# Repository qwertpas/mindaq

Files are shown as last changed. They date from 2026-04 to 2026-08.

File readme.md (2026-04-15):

# mindaq PCB

A cheap and minimal data aquisition system for reading 6-axis force/torque sensors at high rates.

demo

- 2.5V strain gauge excitation using precision reference (REF5025)
- Simultaneous sampling 24-bit ADC (ADS131M08) with 8 channels at 32k samples/second for
    - 6x strain gauges
    - 1x voltage up to 29.4V 
    - 1x current using external low-side shunt resistor
- Controlled by ESP32S3 Supermini dev board (USB-C powered)
- Display live force/torque data on Adafruit color TFT
- 42 x 29 mm board size
- 2-layer, single side components, JLCPCB economic assembly
- About $11 in parts cost per board (including ESP32S3)
- Single order of 2pcs is $70, 5pcs is $120 including everything (shipping and customs about doubles the cost!) 

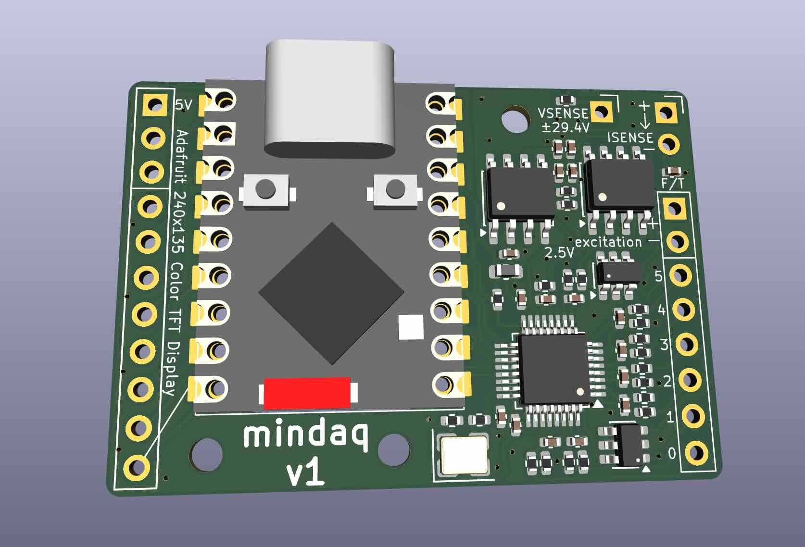
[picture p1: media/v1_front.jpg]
Front Side

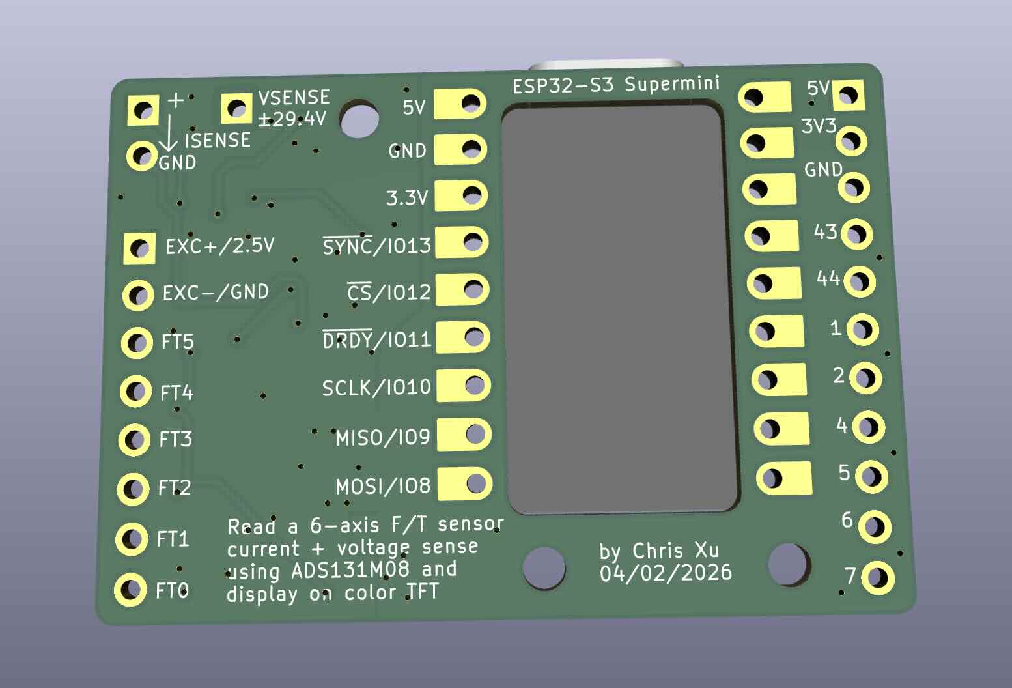
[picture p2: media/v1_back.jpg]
Back Side


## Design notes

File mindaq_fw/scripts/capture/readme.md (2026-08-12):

# Mindaq Capture GUI

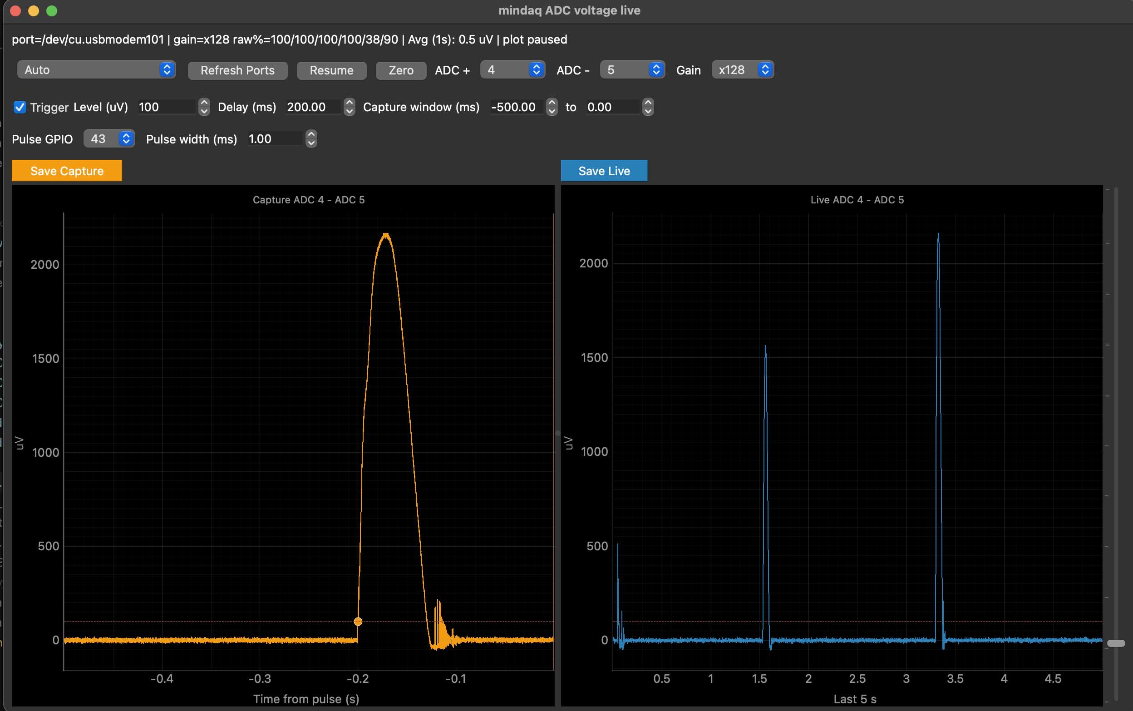
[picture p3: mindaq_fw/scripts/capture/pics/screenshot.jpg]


This GUI streams voltage data from the Mindaq, shows a live rolling plot, and records trigger-aligned captures like an oscilloscope. It also pulses a GPIO pin a configurable delay after the trigger to align external devices (e.g. slow motion camera). Mindaq must be running the capture firmware.

## Usage

Download [capture_gui.py](https://github.com/qwertpas/mindaq/blob/main/mindaq_fw/scripts/capture/capture_gui.py).

Install python libraries if you don't have them:

```bash
python3 -m pip install pyserial pyqtgraph PyQt5
```

Start the GUI:

```bash
python3 capture_gui.py
```

If this does not work on Windows, try replacing `python3` in the above commands with `py -3`.

## Plots

- Live plot (orange): shows the selected ADC voltage over the last 5 seconds. Data is displayed at 1 kHz.
- Capture plot (blue): shows the most recent trigger capture, aligned so GPIO pulse start is at time 0. Data is displayed at 1 kHz.

## Buttons and Settings

- Zeroing: Sets a baseline voltage as a 0 reading by subtracting the average voltage over the last 1 second.
- ADC + and ADC -: select the ADC channels to read from. Channels 6 and 7 are labeled Isense and Vsense. If two channels are selected, the difference is used (useful for load cells).
- Gain: sets the ADC amplifier gain between 1x and 128x. Higher gain means more sensitivity, but could saturate the reading if the voltage is too high (e.g. very high force applied). Check for saturation by looking at the raw% values or whether the live plot is clipping.
- Trigger level: set in microvolts using the numeric field or vertical slider.
- Delay: this amount of time after the trigger threshold crossing, the GPIO pulse starts and is used as the reference for when `capture_time_s` = 0.
- Capture window: you can configure the time window to display and save before and after `capture_time_s` = 0. Default is -500ms to 0ms, meaning it saves and displays the last 500ms before the GPIO pulse start.
- Pulse GPIO: select the GPIO pin to pulse. See labels on the [back of the PCB](https://github.com/qwertpas/mindaq/blob/main/media/v1_back.jpg).
- Pulse width: configurable duration of the GPIO pulse.
- Save Capture: saves the capture window at full 32 kHz sampling rate.
- Save Live: saves the current live buffer at full 32 kHz sampling rate.
- The firmware turns on the built-in red LED when a trigger is accepted and turns it off when the pulse is done.

## Saved CSV data format

Basic:
- `capture_time_s`: time relative to the GPIO pulse start (trigger threshold crossing plus the configured delay). 0 matches the red pulse-start line in the capture plot. The events you care about are likely when `capture_time_s` is slightly negative. <u>Use this to align external devices (e.g. slow motion camera).</u>
- `voltage_zeroed_uv`: Measured voltage after subtracting the current zero offset.
- `voltage_uv`: Measured voltage before zeroing.
- `device_time_s`: Mindaq precise device time since it was powered on.
- `datetime`: wall-clock timestamp estimated from the computer time when saved, used to check roughly when experiment was done. Not as accurate, use `device_time_s` or `capture_time_s` instead for precise timing.

Capture timing columns:
- `trigger_time_s`: device time when the signal crossed the trigger threshold.
- `pulse_start_time_s`: device time when the GPIO pulse starts.
- `pulse_end_time_s`: device time when the GPIO pulse ends.
- `trigger_threshold_uv`: trigger threshold.
- `trigger_cross`: `1` on the sample nearest the trigger crossing.
- `pulse_start`: `1` on the sample nearest pulse start.
- `pulse_active`: `1` for samples during the pulse if the capture window includes them.
- `trigger_gpio`: selected output pin.
- `trigger_edge`: currently always `Rising`, but noise makes it activate on falling edges too.

For debugging:
- `seq`: sample sequence number.
- `pos_channel`, `neg_channel`: selected ADC inputs.
- `adc_N_uv`, `adc_N_raw`: per-channel microvolts and raw ADC counts, paired by channel. ADC 6 is Isense and ADC 7 is Vsense.
- `gain_code`, `warn_flags`, `clip_flags`: stream metadata.

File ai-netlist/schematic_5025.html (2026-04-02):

# minDAQ · Visual Schematic · netlist_5025

ADS131M08 8-ch ADC · 6-ch Force/Torque · ESP32-S3 SuperMini · REF5025 · OPA2333 · SiTime 8.192 MHz

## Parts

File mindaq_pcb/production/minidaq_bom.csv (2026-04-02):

Designator | Footprint | Quantity | Value | LCSC Part #
C1, C11, C2, C3, C4, C7 | 0402 | 6 | 1uF | C52923
C12, C13, C14, C15, C16, C18, C8 | 0402 | 7 | 10nF | C15195
C17 | 0402 | 1 | 1nF | C1523
C5 | 0402 | 1 | 10uF | C15525
C6 | 0402 | 1 | 220nF | C16772
C9 | 0402 | 1 | 0.1uF | C307331
FB1 | 0603 | 1 | BLM18PG121SN1D | C14709
R1 | 0402 | 1 | 33R | C25105
R10, R11, R12, R13, R14, R15, R16, R17, R20, R21, R5, R6, R8, R9 | 0402 | 14 | 100R | C25076
R18, R2, R3, R4, R7 | 0402 | 5 | 47k | C25792
R19 | 0402 | 1 | 2k | C4109
U1 | TQFP-32_5x5mm_P0.5mm | 1 | ADS131M08IPBSR | C2862610
U3 | SOIC-8_3.9x4.9mm_P1.27mm | 1 | REF5025AIDR | C11341
U4 | SOIC-8_3.9x4.9mm_P1.27mm | 1 | OPA2333AIDR | C38732
Y1 | Crystal_SMD_3225-4Pin_3.2x2.5mm | 1 | MST8011AI-22-33E8.192000 | C51026284

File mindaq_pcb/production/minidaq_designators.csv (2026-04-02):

C1:1
C11:1
C12:1
C13:1
C14:1
C15:1
C16:1
C17:1
C18:1
C2:1
C3:1
C4:1
C5:1
C6:1
C7:1
C8:1
C9:1
FB1:1
H1:1
H2:1
H3:1
J1:1
J2:1
J3:1
J6:1
NT1:1
NT2:1
R1:1
R10:1
R11:1
R12:1
R13:1
R14:1
R15:1
R16:1
R17:1
R18:1
R19:1
R2:1
R20:1
R21:1
R3:1
R4:1
R5:1
R6:1
R7:1
R8:1
R9:1
U1:1
U2:1
U3:1
U4:1
U5:1
U6:1
Y1:1

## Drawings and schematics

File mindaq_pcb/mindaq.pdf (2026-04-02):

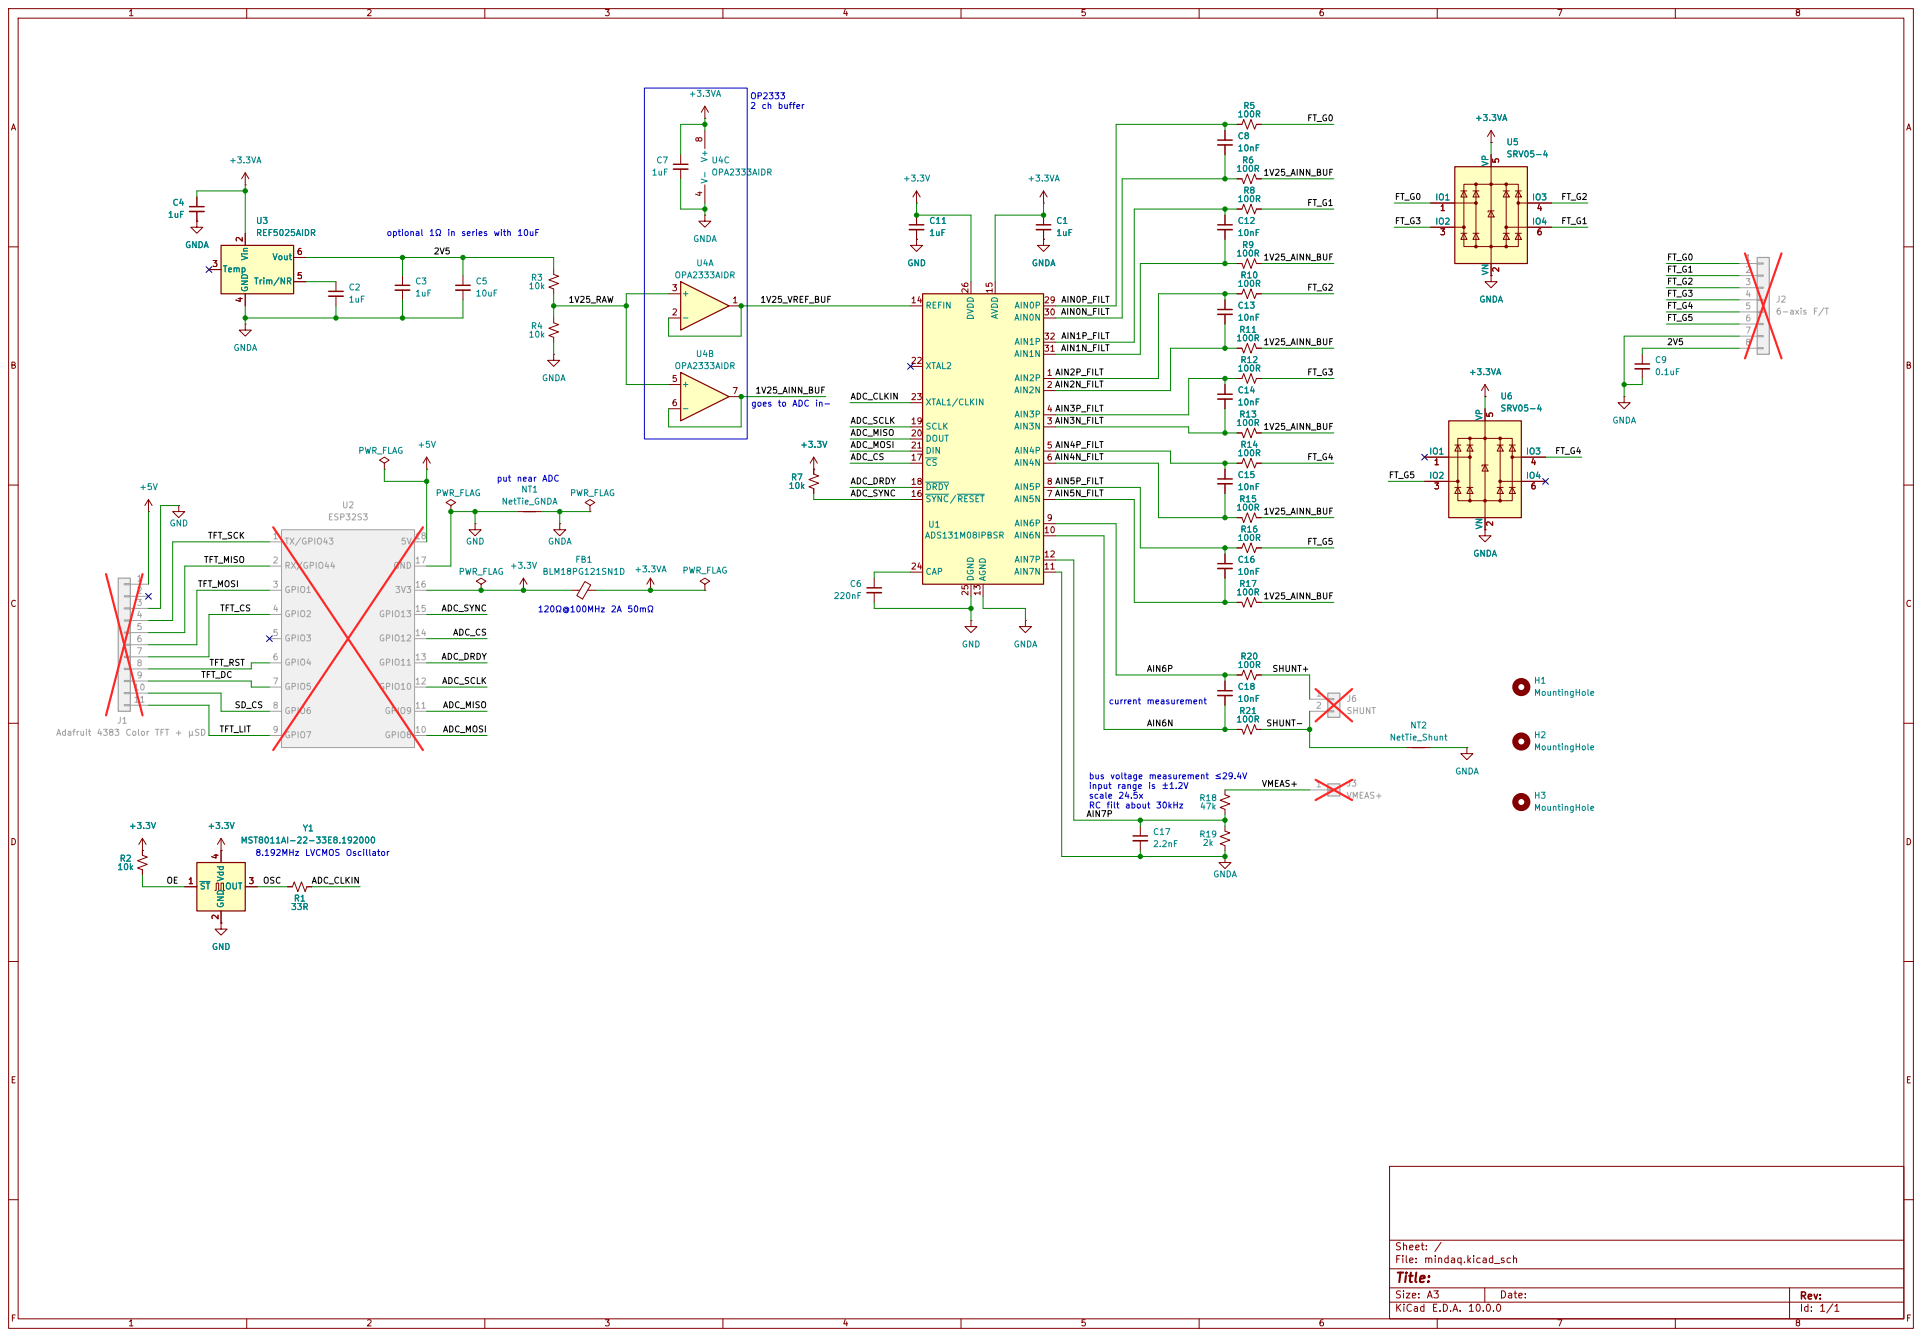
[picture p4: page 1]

2 ch buffer optional 1Ω in series with 10uF

goes to ADC in-

current measurement bus voltage measurement ≤29.4V

Adafruit 4383 Color TFT + μSD

input range is ±1.2V
scale 24.5x RC filt about 30kHz

Size: A3 | Rev: | F Date:
KiCad E.D.A. 10.0.0 | Id: 1/1

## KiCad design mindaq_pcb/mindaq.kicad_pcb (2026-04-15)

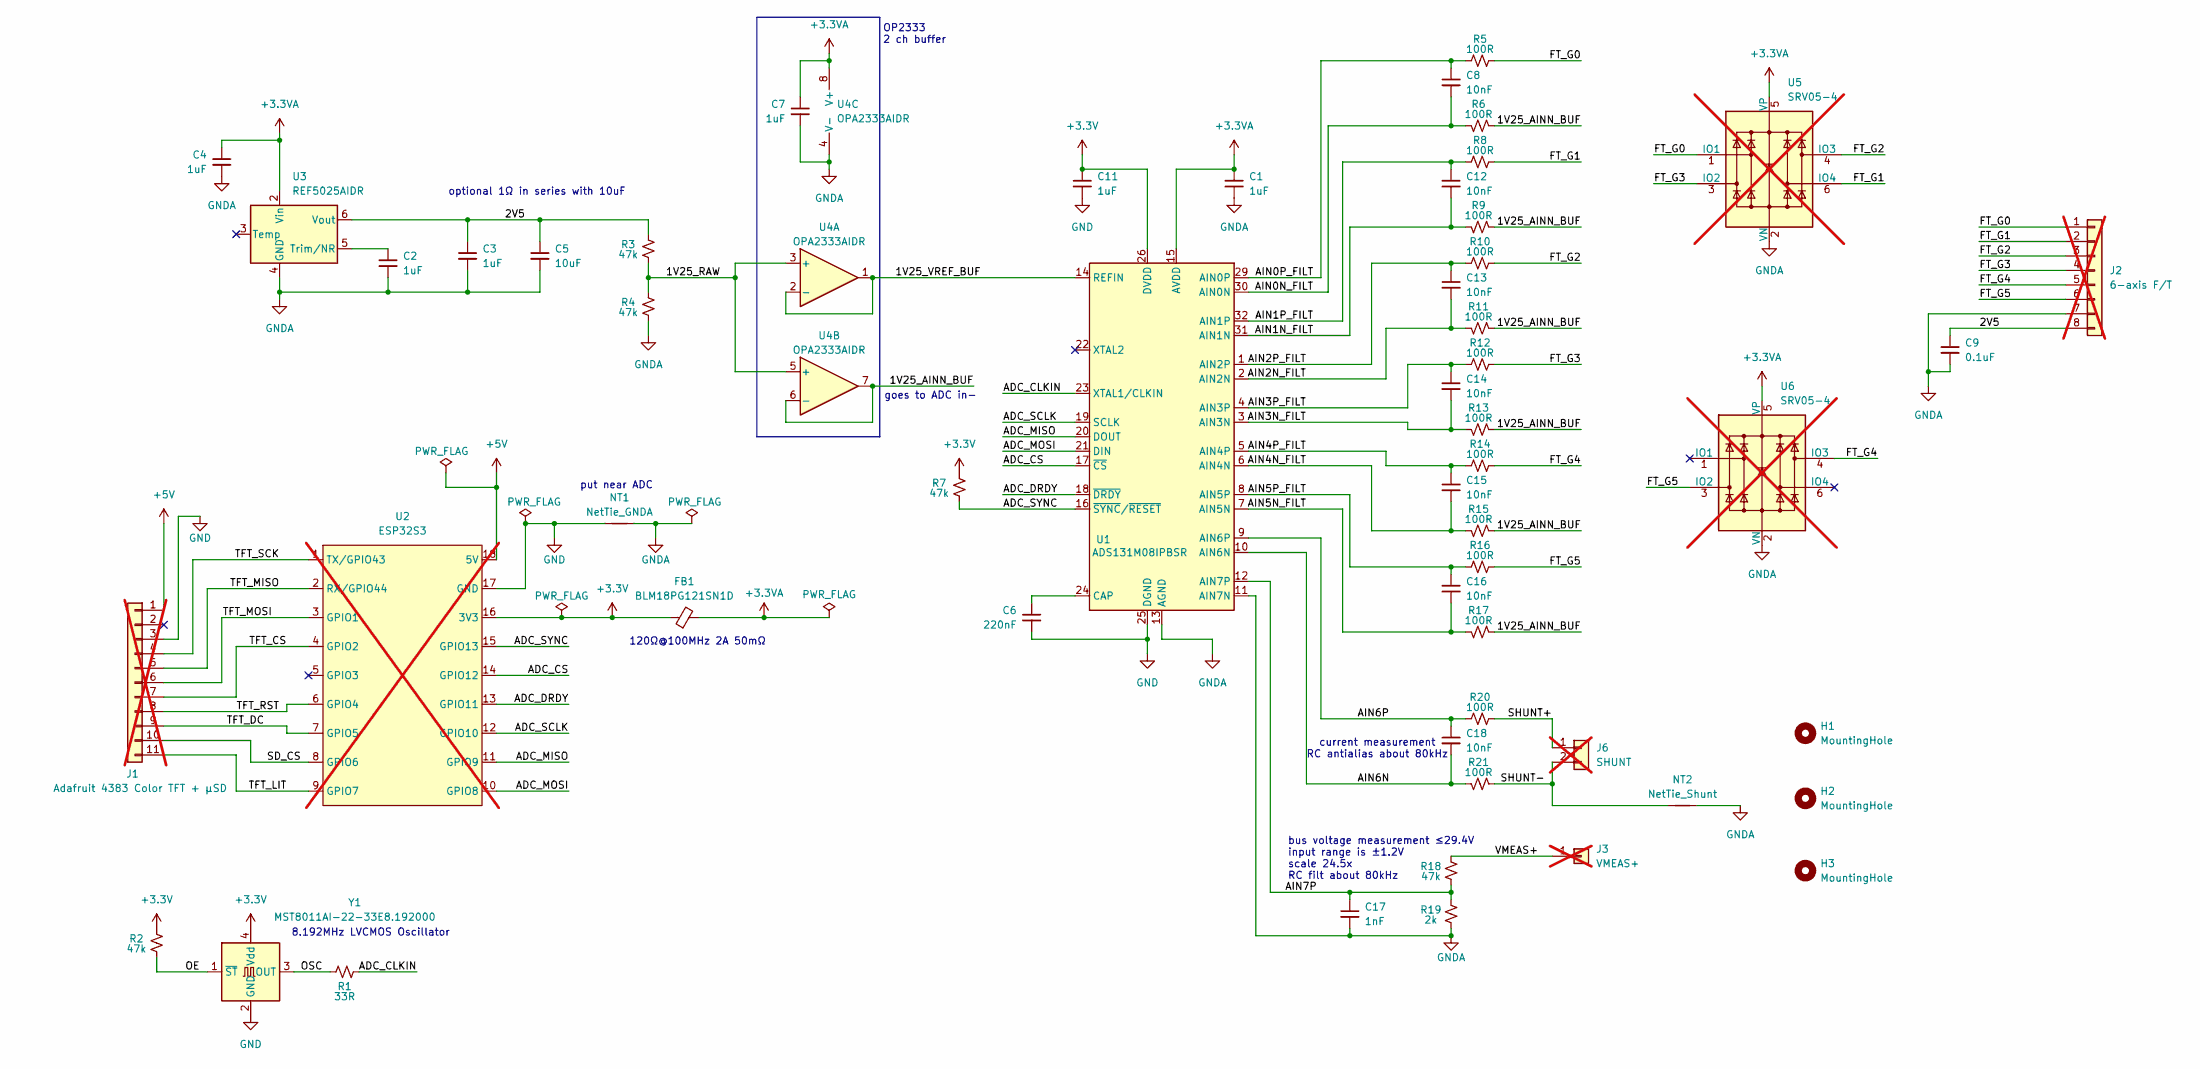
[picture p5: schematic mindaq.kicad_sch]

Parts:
C1, C2, C3, C4, C7, C11: 1uF; C_0402_1005Metric; LCSC C52923
C5: 10uF; C_0402_1005Metric; LCSC C15525
C6: 220nF; C_0402_1005Metric; LCSC C16772
C8, C12, C13, C14, C15, C16, C18: 10nF; C_0402_1005Metric; LCSC C15195
C9: 0.1uF; C_0402_1005Metric; LCSC C307331
C17: 1nF; C_0402_1005Metric; LCSC C1523
FB1: BLM18PG121SN1D; L_0603_1608Metric; LCSC C14709
H1, H2, H3: MountingHole; MountingHole_2.2mm_M2
J1: Adafruit 4383 Color TFT + μSD; PinSocket_1x11_P2.54mm_Vertical; not fitted
J2: 6-axis F/T; PinSocket_1x08_P2.54mm_Vertical; not fitted
J3: VMEAS+; PinSocket_1x01_P2.54mm_Vertical; not fitted
J6: SHUNT; PinSocket_1x02_P2.54mm_Vertical; not fitted
NT1: NetTie_GNDA; NetTie-2_SMD_Pad2.0mm
NT2: NetTie_Shunt; NetTie-2_SMD_Pad0.5mm
R1: 33R; R_0402_1005Metric; LCSC C25105
R2, R3, R4, R7, R18: 47k; R_0402_1005Metric; LCSC C25792
R5, R6, R8, R9, R10, R11, R12, R13, R14, R15, R16, R17, R20, R21: 100R; R_0402_1005Metric; LCSC C25076
R19: 2k; R_0402_1005Metric; LCSC C4109
U1: ADS131M08IPBSR; TQFP-32_5x5mm_P0.5mm; LCSC C2862610
U2: ESP32S3; esp32s3-supermini; not fitted
U3: REF5025AIDR; SOIC-8_3.9x4.9mm_P1.27mm; LCSC C11341
U4: OPA2333AIDR; SOIC-8_3.9x4.9mm_P1.27mm; LCSC C38732
U5, U6: SRV05-4; SOT-23-6; LCSC C20615829; not fitted
Y1: MST8011AI-22-33E8.192000; Crystal_SMD_3225-4Pin_3.2x2.5mm; LCSC C51026284

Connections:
+3.3V: C11.1, FB1.1, R2.1, R7.1, U1.26 (DVDD), U2.16 (3V3), Y1.4 (Vdd)
+3.3VA: C1.1, C4.1, C7.1, FB1.2, U1.15 (AVDD), U3.2 (Vin), U4.8 (V+), U5.5 (VP), U6.5 (VP)
+5V: J1.1, U2.18 (5V)
/1V25_AINN_BUF: R6.2, R9.2, R11.2, R13.2, R15.2, R17.2, U4.6 (-), U4.7
/1V25_RAW: R3.2, R4.1, U4.3 (+), U4.5 (+)
/1V25_VREF_BUF: U1.14 (REFIN), U4.1, U4.2 (-)
/2V5: C3.1, C5.1, C9.1, J2.8, R3.1, U3.6 (Vout)
/ADC_CLKIN: R1.1, U1.23 (XTAL1/CLKIN)
/ADC_CS: U1.17 (~CS), U2.14 (GPIO12)
/ADC_DRDY: U1.18 (~DRDY), U2.13 (GPIO11)
/ADC_MISO: U1.20 (DOUT), U2.11 (GPIO9)
/ADC_MOSI: U1.21 (DIN), U2.10 (GPIO8)
/ADC_SCLK: U1.19 (SCLK), U2.12 (GPIO10)
/ADC_SYNC: R7.2, U1.16 (~SYNC/~RESET), U2.15 (GPIO13)
/AIN0N_FILT: C8.2, R6.1, U1.30 (AIN0N)
/AIN0P_FILT: C8.1, R5.1, U1.29 (AIN0P)
/AIN1N_FILT: C12.2, R9.1, U1.31 (AIN1N)
/AIN1P_FILT: C12.1, R8.1, U1.32 (AIN1P)
/AIN2N_FILT: C13.2, R11.1, U1.2 (AIN2N)
/AIN2P_FILT: C13.1, R10.1, U1.1 (AIN2P)
/AIN3N_FILT: C14.2, R13.1, U1.3 (AIN3N)
/AIN3P_FILT: C14.1, R12.1, U1.4 (AIN3P)
/AIN4N_FILT: C15.2, R15.1, U1.6 (AIN4N)
/AIN4P_FILT: C15.1, R14.1, U1.5 (AIN4P)
/AIN5N_FILT: C16.2, R17.1, U1.7 (AIN5N)
/AIN5P_FILT: C16.1, R16.1, U1.8 (AIN5P)
/AIN6N: C18.2, R21.1, U1.10 (AIN6N)
/AIN6P: C18.1, R20.1, U1.9 (AIN6P)
/AIN7P: C17.1, R18.2, R19.1, U1.12 (AIN7P)
/FT_G0: J2.1, R5.2, U5.1 (IO1)
/FT_G1: J2.2, R8.2, U5.6 (IO4)
/FT_G2: J2.3, R10.2, U5.4 (IO3)
/FT_G3: J2.4, R12.2, U5.3 (IO2)
/FT_G4: J2.5, R14.2, U6.4 (IO3)
/FT_G5: J2.6, R16.2, U6.3 (IO2)
/OE: R2.2, Y1.1 (~ST)
/OSC: R1.2, Y1.3 (OUT)
/SD_CS: J1.10, U2.8 (GPIO6)
/SHUNT+: J6.1, R20.2
/SHUNT-: J6.2, NT2.1, R21.2
/TFT_CS: J1.7, U2.4 (GPIO2)
/TFT_DC: J1.9, U2.7 (GPIO5)
/TFT_LIT: J1.11, U2.9 (GPIO7)
/TFT_MISO: J1.5, U2.2 (RX/GPIO44)
/TFT_MOSI: J1.6, U2.3 (GPIO1)
/TFT_RST: J1.8, U2.6 (GPIO4)
/TFT_SCK: J1.4, U2.1 (TX/GPIO43)
/VMEAS+: J3.1 (Pin_1_1), R18.1
GND: C6.2, C11.2, J1.3, NT1.1, U1.25 (DGND), U2.17 (GND), Y1.2 (GND)
GNDA: C1.2, C2.2, C3.2, C4.2, C5.2, C7.2, C9.2, C17.2, J2.7, NT1.2, NT2.2, R4.2, R19.2, U1.11 (AIN7N), U1.13 (AGND), U1.27 (AGND), U1.28 (AGND), U3.4 (GND), U4.4 (V-), U5.2 (VN), U6.2 (VN)
unnamed: C6.1, U1.24 (CAP)
unnamed: C2.1, U3.5 (Trim/NR)

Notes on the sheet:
OP2333 2 ch buffer
current measurement RC antialias about 80kHz
bus voltage measurement ≤29.4V input range is ±1.2V scale 24.5x RC filt about 80kHz
120Ω@100MHz 2A 50mΩ
goes to ADC in-
optional 1Ω in series with 10uF
put near ADC
8.192MHz LVCMOS Oscillator

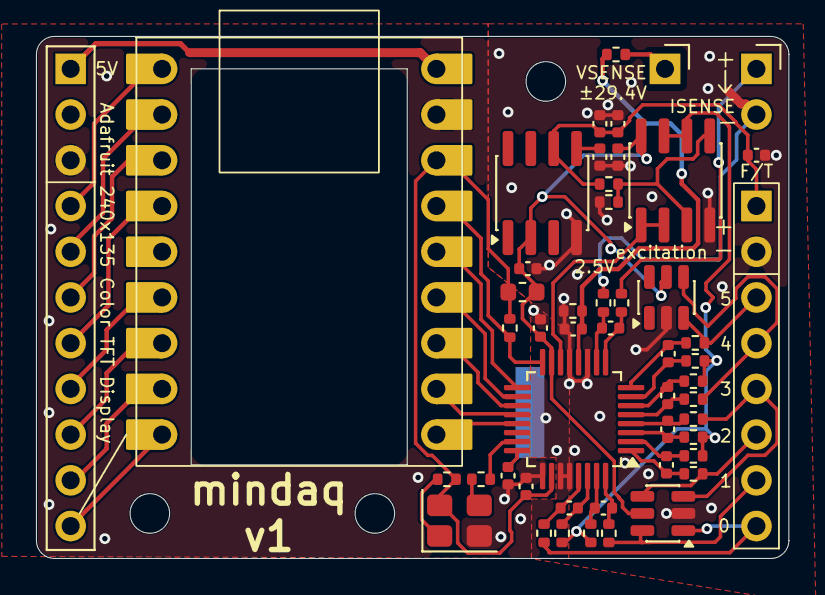
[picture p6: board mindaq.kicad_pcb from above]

Board: 2 copper layers, 41.8 x 29.0 mm, 55 parts (1 on the bottom side), 52 nets.

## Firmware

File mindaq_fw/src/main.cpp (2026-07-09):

#include <Adafruit_GFX.h>
#include <Adafruit_ST7789.h>
#include <Arduino.h>
#include <SPI.h>

namespace {

constexpr uint32_t kSerialBaud = 2000000;
constexpr uint32_t kSpiClockHz = 24000000;
constexpr uint8_t kWords = 10;
constexpr uint8_t kFrameBytes = kWords * 3;
constexpr uint8_t kChannels = 6;
constexpr uint32_t kSync = 0xA55AA55A;
constexpr size_t kSamplesPerBlock = 64;
constexpr size_t kRingSamples = 8192;
constexpr size_t kRingMask = kRingSamples - 1;
constexpr BaseType_t kAdcCore = 0;
constexpr BaseType_t kSerialCore = ARDUINO_RUNNING_CORE;
constexpr BaseType_t kDisplayCore = ARDUINO_RUNNING_CORE;
constexpr UBaseType_t kAdcPriority = 2;
constexpr UBaseType_t kSerialPriority = 1;
constexpr UBaseType_t kDisplayPriority = 1;
constexpr uint32_t kTaskStackBytes = 8192;
constexpr uint32_t kDisplayStackBytes = 8192;
constexpr uint32_t kDisplayRateHz = 10;
constexpr uint32_t kDisplayPeriodMs = 1000 / kDisplayRateHz;
constexpr uint32_t kTftSpiHz = 10000000;
constexpr uint32_t kZeroTimeMs = 1000;
constexpr uint16_t kZeroStepMs = 100;

constexpr uint8_t kAdcSclkPin = 10;
constexpr uint8_t kAdcMisoPin = 9;
constexpr uint8_t kAdcMosiPin = 8;
constexpr uint8_t kAdcDrdyPin = 11;
constexpr uint8_t kAdcCsPin = 12;
constexpr uint8_t kAdcSyncPin = 13;

constexpr uint8_t kTftSclkPin = 43;
constexpr uint8_t kTftMisoPin = 44;
constexpr uint8_t kTftMosiPin = 1;
constexpr uint8_t kTftCsPin = 2;
constexpr uint8_t kTftRstPin = 4;
constexpr uint8_t kTftDcPin = 5;
constexpr uint8_t kSdCsPin = 6;
constexpr uint8_t kTftLitPin = 7;

constexpr uint16_t kModeReg = 0x02;
constexpr uint16_t kClockReg = 0x03;
constexpr uint16_t kGain1Reg = 0x04;
constexpr uint16_t kGain2Reg = 0x05;
constexpr uint16_t kModeValue = 0x0110;
constexpr uint16_t kClockValue32k = 0x3FC2;
constexpr uint8_t kDefaultGainCode = 3;
constexpr uint8_t kMaxGainCode = 7;
constexpr int32_t kAdcFullScale = 0x7FFFFF;
constexpr int32_t kAdcWarnCode = static_cast<int32_t>(static_cast<float>(kAdcFullScale) * 0.85f);
constexpr int32_t kAdcClipCode = static_cast<int32_t>(static_cast<float>(kAdcFullScale) * 0.98f);
constexpr uint8_t kSettleDiscardFrames = 16;

constexpr uint16_t kBgColor = ST77XX_BLACK;
constexpr uint16_t kBorderColor = ST77XX_WHITE;
constexpr uint16_t kTrackColor = ST77XX_BLUE;
constexpr uint16_t kPosColor = ST77XX_GREEN;
constexpr uint16_t kNegColor = ST77XX_RED;
constexpr uint16_t kTextColor = ST77XX_WHITE;
constexpr uint16_t kZeroColor = ST77XX_YELLOW;

constexpr float countToMicrovolt(uint8_t gain_code) {
  return (1.2e6f / static_cast<float>(1u << gain_code)) / 8388608.0f;
}

// Measured no-load ADC means in ADC port order: [port0, port1, port2, port3, port4, port5].
constexpr float kRawZeroCode[kChannels] = {
    -995095.6f, -358128.7f, -940395.8f, -265481.2f, -836644.1f, 18634.5f,
};
constexpr float kRawZeroMicrovolt[kChannels] = {
    kRawZeroCode[0] * countToMicrovolt(kDefaultGainCode),
    kRawZeroCode[1] * countToMicrovolt(kDefaultGainCode),
    kRawZeroCode[2] * countToMicrovolt(kDefaultGainCode),
    kRawZeroCode[3] * countToMicrovolt(kDefaultGainCode),
    kRawZeroCode[4] * countToMicrovolt(kDefaultGainCode),
    kRawZeroCode[5] * countToMicrovolt(kDefaultGainCode),
};

// Converts ADC microvolt deltas to ATI XML gauge order [g0, g1, g2, g3, g4, g5].
// Nonzero locations are the measured wiring:
// port0->g4, port1->g5, port2->g2, port3->g3, port4->g0, port5->g1.
// Nonzero values are the working ADC-count-to-NetFT-gauge bridge (0.016 count/count)
// plus XML GaugeGains normalization from calibration/FT8978 Net.xml.
constexpr float kAdcUvToAtiGauge[kChannels][kChannels] = {
    {0.0f, 0.0f, 0.0f, 0.0f, 1.059662393280649e+00f, 0.0f},
    {0.0f, 0.0f, 0.0f, 0.0f, 0.0f, 8.162949541379004e-01f},
    {0.0f, 0.0f, 9.272045943442637e-01f, 0.0f, 0.0f, 0.0f},
    {0.0f, 0.0f, 0.0f, 9.322712858379332e-01f, 0.0f, 0.0f},
    {8.363021832919449e-01f, 0.0f, 0.0f, 0.0f, 0.0f, 0.0f},
    {0.0f, 8.404218980265711e-01f, 0.0f, 0.0f, 0.0f, 0.0f},
};

// ATI XML gauge order [g0, g1, g2, g3, g4, g5] to [Fx,Fy,Fz,Tx,Ty,Tz].
// Rows other than Fz are from calibration/FT8978 Net.xml, normalized by CountsPerForce
// and CountsPerTorque. Fz is the only fitted row, constrained to the ideal sparse
// normal-gauge pattern and fitted from 41 500 g plate-placement captures.
constexpr float kAtiGaugeToFt[kChannels][kChannels] = {
    {6.054530989079390e-06f, 2.075418832354940e-05f, -9.575586391247820e-06f,
     -5.034719323341890e-04f, -2.827122413565440e-05f, 5.179287349565690e-04f},
    {-2.520127206219610e-05f, 6.348497973460170e-04f, -1.038902452683050e-07f,
     -2.775572866673270e-04f, 8.796242351000440e-06f, -3.247148267647300e-04f},
    {4.838318054700e-04f, 0.0f, 5.434076606576e-04f, 0.0f, 5.993160239162e-04f,
     0.0f},
    {-2.577052836577890e-07f, 3.830766465429980e-06f, 3.124957530622520e-06f,
     -1.381712094274260e-06f, -3.204207898418680e-06f, -2.084386424212550e-06f},
    {-3.172020201011310e-06f, -4.085733997308220e-07f, 1.741821139441800e-06f,
     3.219636663939340e-06f, 2.229410518476670e-06f, -3.070929538864320e-06f},
    {-9.943845273683800e-08f, 2.240688262268020e-06f, 2.397902398001370e-08f,
     2.162107308175090e-06f, -7.705459896268520e-08f, 2.297459226084220e-06f},
};
constexpr float kDisplayFullScale[kChannels] = {
    12.0f, 12.0f, 17.0f, 0.12f, 0.12f, 0.12f,
};

enum class DisplayStatus : uint8_t {
  Boot = 0,
  Retry = 1,
  Zeroing = 2,
  Ready = 3,
};

struct __attribute__((packed)) Sample {
  uint32_t seq;
  uint8_t raw[kChannels * 3];
  uint8_t gain_code;
  uint8_t warn_flags;
  uint8_t clip_flags;
};

struct __attribute__((packed)) Block {
  uint32_t sync;
  uint32_t seq;
  uint8_t raw[kSamplesPerBlock][kChannels * 3];
  uint8_t gain_code;
  uint8_t warn_flags;
  uint8_t clip_flags;
  uint8_t checksum;
};

struct DisplaySnapshot {
  float values[kChannels] = {};
  uint8_t gain_code = kDefaultGainCode;
  DisplayStatus status = DisplayStatus::Boot;
  uint16_t zero_progress = 0;
};

uint8_t tx[kFrameBytes] = {};
uint8_t rx[kFrameBytes] = {};
Sample ring[kRingSamples] = {};
Block block = {};
volatile uint32_t write_index = 0;
volatile uint32_t read_index = 0;
uint32_t seq = 0;
volatile uint8_t current_gain_code = kDefaultGainCode;
volatile uint8_t requested_gain_code = kDefaultGainCode;
volatile bool output_paused = false;
SPIClass tft_spi(HSPI);
Adafruit_ST7789 tft(&tft_spi, kTftCsPin, kTftDcPin, kTftRstPin);
portMUX_TYPE latest_lock = portMUX_INITIALIZER_UNLOCKED;
portMUX_TYPE display_lock = portMUX_INITIALIZER_UNLOCKED;
int32_t latest_raw[kChannels] = {};
uint8_t latest_gain_code = kDefaultGainCode;
bool latest_ready = false;
DisplaySnapshot display_snapshot;
uint32_t zero_start_ms = 0;
uint32_t zero_count = 0;
double zero_sum[kChannels] = {};
float zero_offset[kChannels] = {};
bool zero_done = false;

uint16_t rreg(uint8_t address) {
  return 0xA000u | (static_cast<uint16_t>(address) << 7);
}

uint16_t wreg(uint8_t address) {
  return 0x6000u | (static_cast<uint16_t>(address) << 7);
}

uint16_t gain1Value(uint8_t gain_code) {
  return (static_cast<uint16_t>(gain_code) << 12) | (static_cast<uint16_t>(gain_code) << 8) |
         (static_cast<uint16_t>(gain_code) << 4) | gain_code;
}

uint16_t gain2Value(uint8_t gain_code) {
  return (static_cast<uint16_t>(gain_code) << 4) | gain_code;
}

void putCommand(uint16_t command) {
  memset(tx, 0, sizeof(tx));
  tx[0] = static_cast<uint8_t>(command >> 8);
  tx[1] = static_cast<uint8_t>(command & 0xFF);
}

uint32_t word24(size_t word) {
  const size_t i = word * 3;
  return (static_cast<uint32_t>(rx[i]) << 16) | (static_cast<uint32_t>(rx[i + 1]) << 8) | rx[i + 2];
}

int32_t signExtend24(uint32_t word) {
  int32_t value = static_cast<int32_t>(word & 0x00FFFFFFu);
  if ((value & 0x00800000) != 0) {
    value |= ~0x00FFFFFF;
  }
  return value;
}

uint32_t rawLe24(const uint8_t *raw) {
  return static_cast<uint32_t>(raw[0]) | (static_cast<uint32_t>(raw[1]) << 8) |
         (static_cast<uint32_t>(raw[2]) << 16);
}

bool waitDrdy() {
  const uint32_t start = micros();
  while (digitalRead(kAdcDrdyPin) == LOW) {
    if (micros() - start > 50000) {
      return false;
    }
  }
  while (digitalRead(kAdcDrdyPin) != LOW) {
    if (micros() - start > 50000) {
      return false;
    }
  }
  return true;
}

bool transfer() {
  if (!waitDrdy()) {
    return false;
  }
  SPI.beginTransaction(SPISettings(kSpiClockHz, MSBFIRST, SPI_MODE1));
  digitalWrite(kAdcCsPin, LOW);
  SPI.transferBytes(tx, rx, kFrameBytes);
  digitalWrite(kAdcCsPin, HIGH);
  SPI.endTransaction();
  return true;
}

bool writeRegister(uint8_t address, uint16_t value) {
  putCommand(wreg(address));
  tx[3] = static_cast<uint8_t>(value >> 8);
  tx[4] = static_cast<uint8_t>(value & 0xFF);
  if (!transfer()) {
    return false;
  }
  putCommand(0);
  if (!transfer()) {
    return false;
  }
  return static_cast<uint16_t>(word24(0) >> 8) == static_cast<uint16_t>(0x4000u | (address << 7));
}

bool writeGainRegisters(uint8_t gain_code) {
  return writeRegister(kGain1Reg, gain1Value(gain_code)) &&
         writeRegister(kGain2Reg, gain2Value(gain_code));
}

bool readRegister(uint8_t address, uint16_t &value) {
  putCommand(rreg(address));
  if (!transfer()) {
    return false;
  }
  putCommand(0);
  if (!transfer()) {
    return false;
  }
  value = static_cast<uint16_t>(word24(0) >> 8);
  return true;
}

void startStreamSpi() {
  memset(tx, 0, sizeof(tx));
  SPI.beginTransaction(SPISettings(kSpiClockHz, MSBFIRST, SPI_MODE1));
}

void stopStreamSpi() {
  SPI.endTransaction();
}

bool readStreamFrame() {
  if (!waitDrdy()) {
    return false;
  }
  digitalWrite(kAdcCsPin, LOW);
  SPI.transferBytes(tx, rx, kFrameBytes);
  digitalWrite(kAdcCsPin, HIGH);
  return true;
}

uint8_t blockChecksum(const Block &block) {
  const auto *bytes = reinterpret_cast<const uint8_t *>(&block);
  uint8_t value = 0;
  for (size_t i = 0; i + 1 < sizeof(block); ++i) {
    value ^= bytes[i];
  }
  return value;
}

uint8_t saturationFlag(int32_t value, int32_t threshold) {
  const int32_t magnitude = value < 0 ? -value : value;
  return magnitude >= threshold ? 1 : 0;
}

void fillSample(Sample &sample, uint32_t sample_seq) {
  sample.seq = sample_seq;
  sample.gain_code = current_gain_code;
  sample.warn_flags = 0;
  sample.clip_flags = 0;
  for (size_t ch = 0; ch < kChannels; ++ch) {
    const uint32_t value = word24(ch + 1);
    sample.raw[ch * 3 + 0] = static_cast<uint8_t>(value & 0xFF);
    sample.raw[ch * 3 + 1] = static_cast<uint8_t>((value >> 8) & 0xFF);
    sample.raw[ch * 3 + 2] = static_cast<uint8_t>((value >> 16) & 0xFF);
    const int32_t raw = signExtend24(value);
    sample.warn_flags |= saturationFlag(raw, kAdcWarnCode) << ch;
    sample.clip_flags |= saturationFlag(raw, kAdcClipCode) << ch;
  }
  if ((sample_seq & 0x1F) == 0) {
    portENTER_CRITICAL(&latest_lock);
    for (size_t ch = 0; ch < kChannels; ++ch) {
      latest_raw[ch] = signExtend24(rawLe24(&sample.raw[ch * 3]));
    }
    latest_gain_code = sample.gain_code;
    latest_ready = true;
    portEXIT_CRITICAL(&latest_lock);
  }
}

bool applyRequestedGain() {
  const uint8_t gain_code = requested_gain_code;
  if (gain_code == current_gain_code) {
    return true;
  }
  output_paused = true;
  vTaskDelay(1);
  stopStreamSpi();
  const bool ok = writeGainRegisters(gain_code);
  startStreamSpi();
  if (ok) {
    current_gain_code = gain_code;
    for (uint8_t i = 0; i < kSettleDiscardFrames; ++i) {
      readStreamFrame();
    }
    write_index = 0;
    read_index = 0;
    seq = 0;
    latest_ready = false;
  } else {
    requested_gain_code = current_gain_code;
  }
  output_paused = false;
  return ok;
}

void handleCommand(char *command) {
  if (strncmp(command, "gain ", 5) != 0) {
    return;
  }
  char *end = nullptr;
  const long value = strtol(command + 5, &end, 10);
  if (end == command + 5 || value < 0 || value > kMaxGainCode) {
    return;
  }
  requested_gain_code = static_cast<uint8_t>(value);
}
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

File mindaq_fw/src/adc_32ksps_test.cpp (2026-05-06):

#include <Arduino.h>
#include <SPI.h>

namespace {

constexpr uint32_t kSerialBaud = 2000000;
constexpr uint32_t kSpiClockHz = 24000000;
constexpr uint8_t kWords = 10;
constexpr uint8_t kBytes = kWords * 3;
constexpr uint8_t kChannels = 6;
constexpr uint32_t kSamplesPerBatch = 32000;

constexpr uint8_t kAdcSclkPin = 10;
constexpr uint8_t kAdcMisoPin = 9;
constexpr uint8_t kAdcMosiPin = 8;
constexpr uint8_t kAdcDrdyPin = 11;
constexpr uint8_t kAdcCsPin = 12;
constexpr uint8_t kAdcSyncPin = 13;

constexpr uint16_t kModeReg = 0x02;
constexpr uint16_t kClockReg = 0x03;
constexpr uint16_t kGain1Reg = 0x04;
constexpr uint16_t kGain2Reg = 0x05;
constexpr uint16_t kModeValue = 0x0110;
constexpr uint16_t kClockValue32k = 0x3FC2;
constexpr uint8_t kGainCode = 3;
constexpr uint16_t kGain1Value =
    (kGainCode << 12) | (kGainCode << 8) | (kGainCode << 4) | kGainCode;
constexpr uint16_t kGain2Value = (kGainCode << 4) | kGainCode;

uint8_t tx[kBytes] = {};
uint8_t rx[kBytes] = {};

uint16_t rreg(uint8_t address) {
  return 0xA000u | (static_cast<uint16_t>(address) << 7);
}

uint16_t wreg(uint8_t address) {
  return 0x6000u | (static_cast<uint16_t>(address) << 7);
}

void putCommand(uint16_t command) {
  memset(tx, 0, sizeof(tx));
  tx[0] = command >> 8;
  tx[1] = command & 0xFF;
}

uint32_t word24(size_t word) {
  const size_t i = word * 3;
  return (static_cast<uint32_t>(rx[i]) << 16) | (static_cast<uint32_t>(rx[i + 1]) << 8) | rx[i + 2];
}

int32_t signExtend24(uint32_t word) {
  int32_t value = static_cast<int32_t>(word & 0x00FFFFFFu);
  if ((value & 0x00800000) != 0) {
    value |= ~0x00FFFFFF;
  }
  return value;
}

bool waitDrdy(uint32_t &ready_us) {
  const uint32_t start = micros();
  while (digitalRead(kAdcDrdyPin) != LOW) {
    if (micros() - start > 50000) {
      return false;
    }
  }
  ready_us = micros();
  return true;
}

bool transfer(uint32_t &ready_us, uint32_t &transfer_us) {
  if (!waitDrdy(ready_us)) {
    return false;
  }
  const uint32_t start = micros();
  SPI.beginTransaction(SPISettings(kSpiClockHz, MSBFIRST, SPI_MODE1));
  digitalWrite(kAdcCsPin, LOW);
  SPI.transferBytes(tx, rx, kBytes);
  digitalWrite(kAdcCsPin, HIGH);
  SPI.endTransaction();
  transfer_us = micros() - start;
  return true;
}

bool writeRegister(uint8_t address, uint16_t value) {
  uint32_t ready = 0;
  uint32_t took = 0;
  putCommand(wreg(address));
  tx[3] = value >> 8;
  tx[4] = value & 0xFF;
  if (!transfer(ready, took)) {
    return false;
  }
  putCommand(0);
  if (!transfer(ready, took)) {
    return false;
  }
  return static_cast<uint16_t>(word24(0) >> 8) == static_cast<uint16_t>(0x4000u | (address << 7));
}

bool readRegister(uint8_t address, uint16_t &value) {
  uint32_t ready = 0;
  uint32_t took = 0;
  putCommand(rreg(address));
  if (!transfer(ready, took)) {
    return false;
  }
  putCommand(0);
  if (!transfer(ready, took)) {
    return false;
  }
  value = word24(0) >> 8;
  return true;
}
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

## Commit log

2026-04-02 generate production files for jlcpcb
    [mindaq.kicad_pcb, mindaq.kicad_sch, minidaq_bom.csv, minidaq_designators.csv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]
2026-04-15 mindaq fw and gui works with rough mapping
    [mindaq.kicad_pcb, minidaq_positions.csv]
2026-04-20 FT8978 calibration
2026-04-20 use 6x6 factory calibration for FT8978
2026-05-06 try 32ksps adc read and stream
    [firstjump.csv, jump2.csv, jump3.csv]
2026-05-07 calibrated and adjustabl gain
2026-05-24 add the whole gain range, raw adc streaming
    [firstjump.csv, jump2.csv, jump3.csv]
